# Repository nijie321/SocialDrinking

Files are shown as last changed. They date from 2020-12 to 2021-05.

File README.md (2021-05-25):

# PeerPub 
 Tracking two rats independently during oral operant self-administration of solutions (e.g. sucrose, alcohol, opioids).

## Program Structure

   Main Program: main.py (main_test.py) is the entry program. This program handles session command and rat ID
   scanning, adjusting the pump position, and finally calling the operant.py as a subprocess.
   Note that this program does not exit after calling the subprocess. It it kept alive, as the
   main thread, to record rat's ID when they poke their head near the antenna. Rat's ID are
   stored in _active and _inactive files located in the /home/pi/ directory.
   
   Operant Program: operant.py (operant_test.py) is the program which main invoke at the end of it's executation.
   This program handles saving each data point to corresponding data files.

   Pump Driver Program: pump_move.py is the program that is used, as a higher level abstraction, to drive the stepper motor using underlying gpiozero/RPi.GPIO library. This program mainly consist of the PumpMove class which contains a move() class for "rotating" the motor (forward and backward). The __del__ method need to be call at the end of each use to 'shutoff' the motor. This prevent the motor driver from overheating (there are more efficient ways to do this).
   
   Activity Counter Program: Rat's activity (inactive lick, active lick, and etc) are being represent as an instance of RatActivityCounter.

   PumpCalibration Program: Currently, the motor step size is not accurate enough. The pump's step need to be modified from time to time. This program prompt the user to measure the amount of solution the pump push out and enter that amount. Then the program will automatically re-adjust the step size.

## Configuration
   - Files

     - /home/pi/peerpub_config.json
        This file stores 3 information: device ID, session number/ID, and stepper motor step size. (The session number is increament by 1 each time the program start)

     - /home/pi/openbehavior/PeerPub/python/session_configuration.csv
        This file is used by the program to read in the session information. 

     - /home/pi/openbehavior/PeerPub/python/config.py
        This file stores different directory paths. Note that these path are all absolute paths. There's a "get_sessioninfo" function which takes in a argument "sessionid" to retrive session information from "session_configuration.csv" mentioned above. A good practice is to put related configuration functions in this file and import then when needed.

## Utility Scripts

   **check_empty_program.sh**: a script that check the size of every python file in the python/ directory. If one or more files are empty the script then reclone the entire repository.

   **check_network.sh**: a script that check the network connection right after the device boots up and ask user for action when the device was not able to connect to network.

## Program Overview
The main (main_test.py) program is used to read/scan the pre-configured command RFID stored in 'session_configuration.csv' file under python directory. After the command ID is scaned, the program proceed to ask for scanning rat's ID. The time between scanning rat's ID and command ID is the time for adjusting the pump position (e.g. after the rat's ID are scanned, the pump adjustment are disabled to avoid driver board overheating). After the rat's ID are scanned, the main program spawns a new operant (operant_test.py) program by passing in the necessary arguments and run it in the background. Note that because the operant program is a thread, the main program is kept alive (e.g. running in parallel with the operant program). The main program is tasked with reading the rat's ID when they poke their head into the active or inactve spout (disctinguished by the length of characters: 10 for inactive poke and 8 for active poke).

## Parts and GPIO Pin Connections Table

   [DRV8834 Low-Voltage Stepper Motor Driver](https://www.pololu.com/product/2134), [Stepper Motor](https://www.pololu.com/product/2267), [Belker Universal AC Adapter 3-12V](https://www.amazon.com/Belker-Adjustable-Universal-Household-Electronics/dp/B07NKZCWT1/ref=asc_df_B07NKZCWT1/?tag=hyprod-20&linkCode=df0&hvadid=366402536789&hvpos=&hvnetw=g&hvrand=9548953669677245441&hvpone=&hvptwo=&hvqmt=&hvdev=c&hvdvcmdl=&hvlocint=&hvlocphy=9013532&hvtargid=pla-800552094134&psc=1&tag=&ref=&adgrpid=75347436439&hvpone=&hvptwo=&hvadid=366402536789&hvpos=&hvnetw=g&hvrand=9548953669677245441&hvqmt=&hvdev=c&hvdvcmdl=&hvlocint=&hvlocphy=9013532&hvtargid=pla-800552094134)
   | Pins on the driver | GPIO pin slot on the Pi, external power supply, and the stepper motor|
   |--------------------|------------------------|
   |      VMOT         |      **AC Adapter** - positive end of LED Terminal Adapter    |
   |     GND |   **AC Adapter** - negative end of LED Terminal Adapter |
   | B2, B1, A1, A2 |    **Stepper Motor** - Black, Green, Red, and Blue wire respectively      |
   |      GND |    **Pi** - Any GND pin                |
   |      M0, M1 | **Pi** - GPIO 17 and 22       |
   |     SLP | **Pi** - Any 3v3 pin          |
   |      STEP | **Pi** - GPIO 6            |
   |      DIR | **Pi** - GPIO 26 |
   
   [Adafruit 12-Key Capacitive Touch Sensor - MPR121](https://www.adafruit.com/product/1982)
   | Pins on the driver | GPIO pin slot on the Pi and external wires|
   |--------------------|------------------------|
   |  SCL, SDA | **Pi** - GPIO 3 and 2 respectively |
   |  3Vo | **Pi** - Any 3v3 pin|
   |  GND | **Pi** - Any GND pin|
   |  0 | **external wire** - inactive wire|
   |  1 | **external wire** - active wire|

   [Limit Switch](https://www.amazon.com/MXRS-Hinge-Momentary-Button-Switch/dp/B07MW2RPJY/ref=lp_5739467011_1_7)
   | Pins on the driver | GPIO pin slot on the Pi and external wires|
   |--------------------|------------------------|
   |  Normally Open (NO) | **Pi** - any GND pin|
   |  Forward Limit - Contact Point (C) | **Pi** - GPIO 24|
   |  Backward Limit - Contact Point (C) | **Pi** - GPIO 23|

   [Push Button](https://www.amazon.com/DAOKI-Miniature-Momentary-Tactile-Quality/dp/B01CGMP9GY/ref=asc_df_B01CGMP9GY/?tag=hyprod-20&linkCode=df0&hvadid=309774137275&hvpos=&hvnetw=g&hvrand=7843520885449353644&hvpone=&hvptwo=&hvqmt=&hvdev=c&hvdvcmdl=&hvlocint=&hvlocphy=9013532&hvtargid=pla-640514760452&psc=1)
   | Pins on the driver | GPIO pin slot on the Pi|
   |--------------------|------------------------|
   | Forward Button | **Pi** - GPIO 5|
   | Backward Button | **Pi** - GPIO 27|
   **Connect resistor and GND correspondingly**
   
   [Pixel Ring](https://www.adafruit.com/product/1643)
   | Pins on the driver | GPIO pin slot on the Pi|
   |--------------------|------------------------|
   | IN | **Pi** - GPIO 18|
   | GND | **Pi** - any GND pin |
   | 5V DC | **Pi** - any 5V pin |

## Resources
   [Raspberry Pi Stepper Motor Tutorial](https://www.rototron.info/raspberry-pi-stepper-motor-tutorial/)  
   [Raspberry Pi Stepper Motor Control with nema17](https://makersportal.com/blog/raspberry-pi-stepper-motor-control-with-nema-17)  
   [OpenSourceSyringePump](http://cavarnon.com/syringepump)  
   [How to Control a stepper motor with DRV8825 driver and Arduino](https://www.makerguides.com/drv8825-stepper-motor-driver-arduino-tutorial/)

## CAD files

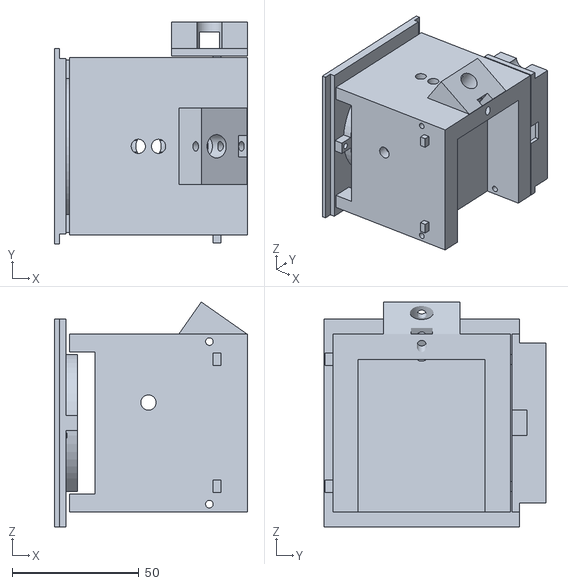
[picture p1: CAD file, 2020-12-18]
openscad/rfid_waterspout_complete.stl
76.0 x 87.5 x 88.6

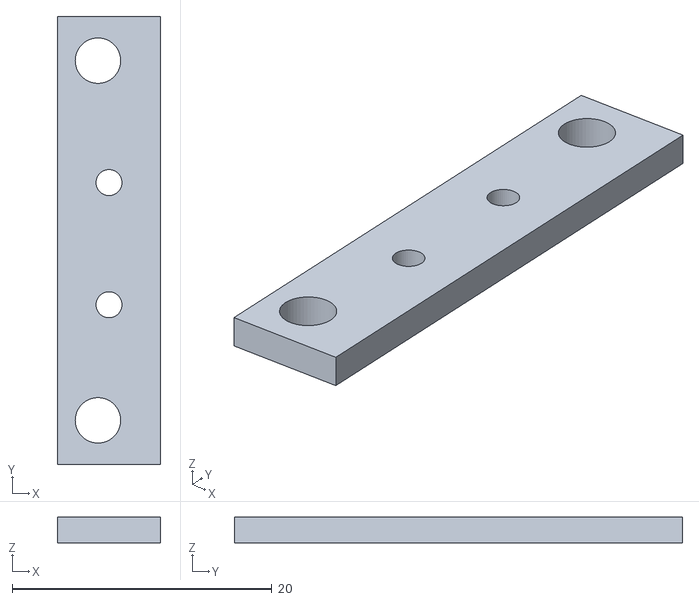
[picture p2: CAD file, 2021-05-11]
openscad/limit_button_mount.stl
7.90 x 34.5 x 2.00

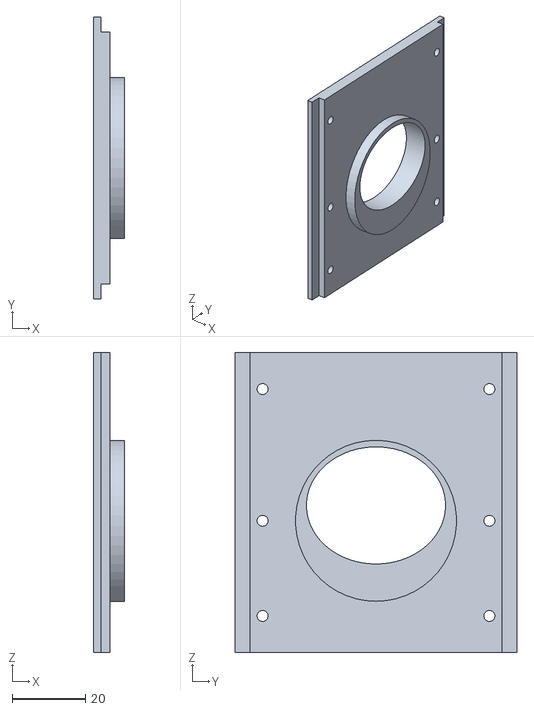
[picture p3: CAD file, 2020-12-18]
openscad/rfid_waterspout_front_panel.stl
8.50 x 77.0 x 82.0

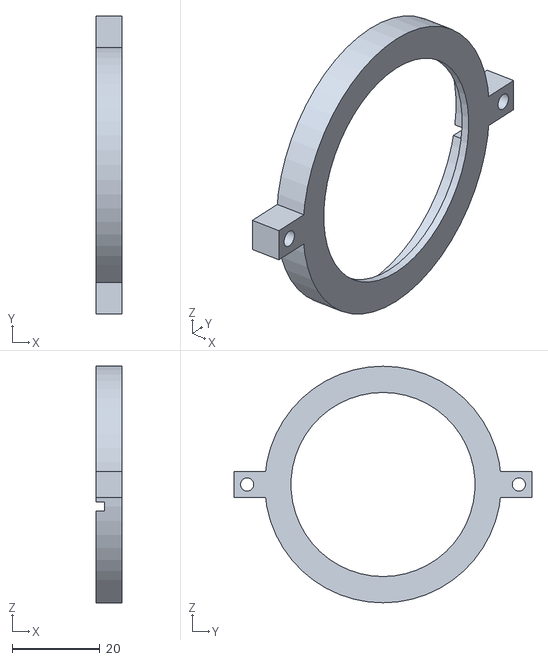
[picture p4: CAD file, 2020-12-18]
openscad/rfid_waterspout_ring_cover.stl
6.00 x 68.0 x 54.0

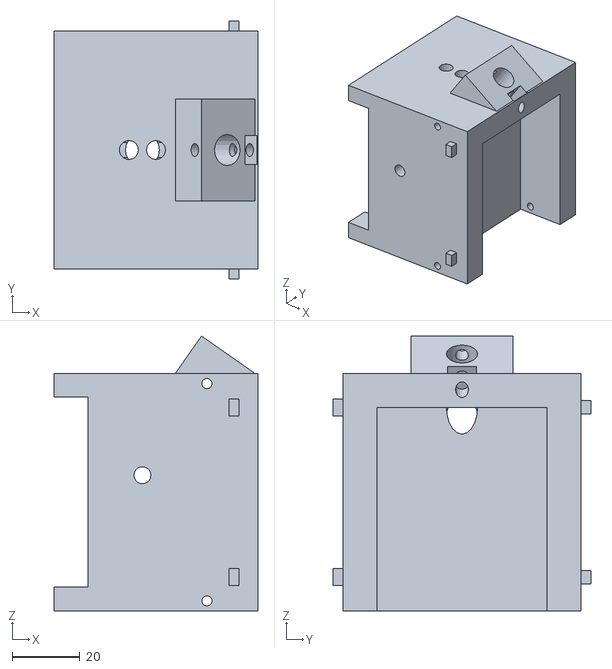
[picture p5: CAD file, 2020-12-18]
openscad/rfid_waterspout_holder.stl
60.0 x 76.0 x 81.0

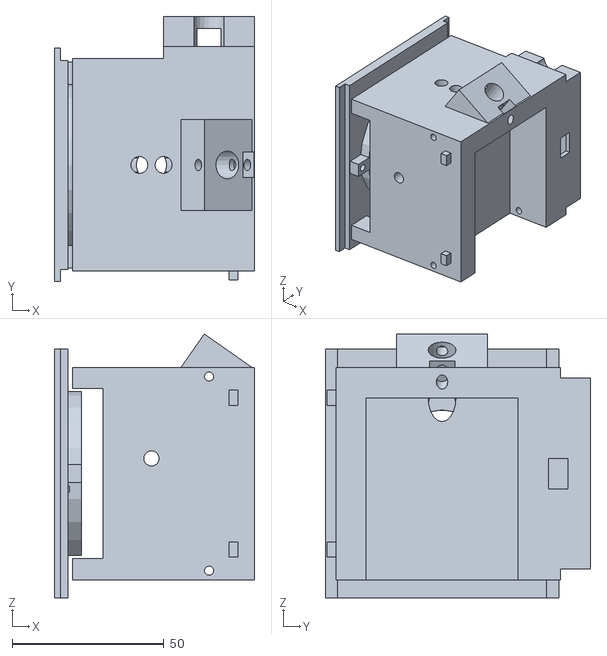
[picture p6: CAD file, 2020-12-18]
openscad/rfid_waterspout_entire_unit.stl
66.0 x 87.5 x 87.0

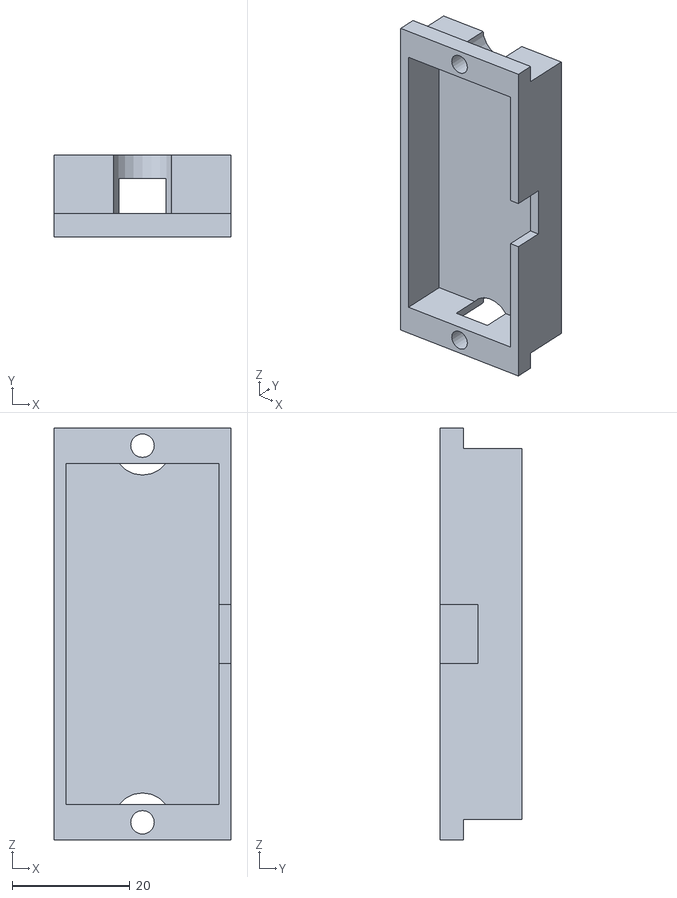
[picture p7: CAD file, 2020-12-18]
openscad/rfid_water_spout_cboard_cover.stl
30.0 x 14.0 x 70.0

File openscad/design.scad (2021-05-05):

$fn=50;


height=59.35 - 2.4;
width=47.60;
thickness=10.65;

topWidth=38.29;
topHeight=23.70;
bottomWidth=31.10;
bottomHeight=height-topHeight;
thickness3=6.57;



diameter=28.88;



circleThickness=2;
radius=diameter/2 + 1;

smallRecHeight=8.38;
smallRecWidth=3.33;
cuttingWidth=23.59;
cuttingHeight=14.69;
extraHeight = (height - (smallRecHeight + cuttingHeight));
extraWidth = 3.63;

bigCircleDiameter=27.33;
topHalfHeight=29.63;
remaindingHeight=height-topHalfHeight;

hex_nut_diameter=7.89 + 1.6; // +1.6, 
hex_nut_radius=hex_nut_diameter/2;
hex_nut_thickness=3.85;

hex_nut_inner_diameter= 5.8;//5;
hex_nut_inner_radius=hex_nut_inner_diameter/2 + .4;



temp=(thickness/2) - (thickness - thickness3);
offsetFromCenter=19; //19.25; //1.5 // 2.3
hexNutGroveExtraDepth=2;

screwRadius=1.75;
screwDepth=9.35;

module part1(){
translate([(width/2) - (topWidth/2) ,(thickness/2) - (thickness3)/2,0]) color("blue") difference(){    
    difference(){
cube([topWidth, thickness3, height], center=true);  

union(){
color("blue") translate([topWidth/2 - (extraWidth/2),0,-extraHeight/2 + ( (height/2) - (smallRecHeight + cuttingHeight) )]) cube([extraWidth,thickness3 ,extraHeight],center=true);

color("blue") translate([ -(topWidth/2 - (extraWidth/2)),0,-extraHeight/2 + ( (height/2) - (smallRecHeight + cuttingHeight) )]) cube([extraWidth,thickness3 ,extraHeight],center=true);
}


//translate([0,0,extraHeight - (height/2) - offsetFromCenter]) union(){
//    //-(remaindingHeight/2) + (hex_nut_radius)
//translate([0,5,0]) color("black") rotate([90,0,0]) cylinder(h=hex_nut_thickness/2 + hexNutGroveExtraDepth + 1.3, r=hex_nut_radius,center=true, $fn = 6); //h=thickness3
////-(remaindingHeight/2) + (hex_nut_inner_radius + (hex_nut_radius - hex_nut_inner_radius))
//translate([0, 0,0]) color("red") rotate([90,0,0]) cylinder(h=hex_nut_thickness/2 + 10, r=hex_nut_inner_radius,center=true, $fn = 6);
//}


}
union(){
    translate([0,-((-(thickness3/2)+(thickness3-circleThickness)/2)),(height/2) - (smallRecHeight + cuttingHeight) ]) union(){
translate([0,0,(cuttingHeight/2) + (smallRecHeight)]) cube([cuttingWidth,thickness3 - circleThickness +.1, cuttingHeight],center=true);
                 translate([0,0,smallRecHeight/2]) cube([smallRecWidth,thickness3 - circleThickness+.1,smallRecHeight],center=true);            
}


translate([0,-(thickness3/2 - (circleThickness/2)),(height/2) - (radius)]) color("red")rotate([90,0,0])union(){
        cylinder(h=circleThickness, r=radius, center=true);
        translate([0,radius/2,0])cube([radius*2,radius,circleThickness],center=true);
    }
    
    }

}
}


module part2(){
//translate([0,temp,0]) 
difference(){
cube([width,thickness,height],center=true);
//translate([0,(thickness/2) - (thickness - thickness3)/2,0]) color("blue") cube([topWidth,thickness - thickness3,height],center=true);
//
translate([(width/2) - (topWidth/2),(thickness/2) - (thickness3)/2,0]) color("blue") union(){
cube([topWidth, thickness3, height], center=true);   
union(){
color("red") translate([topWidth/2 - (extraWidth/2),0,-extraHeight/2 + ( (height/2) - (smallRecHeight + cuttingHeight) )]) cube([extraWidth,thickness3+10 ,extraHeight],center=true);

color("red") translate([ -(topWidth/2 - (extraWidth/2)),0,-extraHeight/2 + ( (height/2) - (smallRecHeight + cuttingHeight) )]) cube([extraWidth,thickness3+10,extraHeight],center=true);
}


//translate([0,0, extraHeight - (height/2)  - offsetFromCenter]) union(){
//    
//translate([0, -temp - (hex_nut_thickness/2) - .8,0]) color("red") rotate([90,0,0]) cylinder(h=hex_nut_thickness/2 + hexNutGroveExtraDepth, r=hex_nut_radius,center=true, $fn = 6);
//
//translate([0, -temp - (hex_nut_thickness/2),0]) color("red") rotate([90,0,0]) cylinder(h=hex_nut_thickness/2 + 7, r=hex_nut_inner_radius,center=true, $fn = 6);
//}


}
}

}

module glueScrews(){
translate([0,0.1,0]) union(){
rotate([90,0,0]) translate([(width/2) - (topWidth/2) - (topWidth/4),-(height/3),-(thickness-screwDepth)/2]) cylinder(h=screwDepth,r=screwRadius,center=true);

rotate([90,0,0]) translate([(width/2) - (topWidth/2) + (topWidth/4),-(height/9),-(thickness-screwDepth)/2]) cylinder(h=screwDepth,r=screwRadius,center=true);
}
}


module modifiedParts(part=1){


difference(){
    
        if(part == 1){
            part1();
        }else if(part == 2){
            part2();
        }
//        part2();    

    
//translate([(width/2) - (topWidth/2),0,extraHeight - (height/2) - offsetFromCenter]) union(){
//    //-(remaindingHeight/2) + (hex_nut_radius)
//    
//    //((hex_nut_thickness/2 + 10)/2)-(hex_nut_thickness/2 + hexNutGroveExtraDepth + 1.3)/2
//
//    
////-(remaindingHeight/2) + (hex_nut_inner_radius + (hex_nut_radius - hex_nut_inner_radius))
//
//
//translate([0,0,0]) color("black") rotate([90,0,0]) cylinder(h=hex_nut_thickness, r=hex_nut_radius,center=true, $fn = 6); //h=thickness3
//
//translate([0, 0,0]) color("red") rotate([90,0,0]) cylinder(h=hex_nut_thickness+ 20, r=hex_nut_inner_radius,center=true, $fn = 6);
//    
//
////    glueScrews();
//}

}
}

//translate([3.5,11,0]) cylinder(d=21.95,h=3.5,$fn=50,center=true);

//translate([(width/2) - (topWidth/2),-(extraHeight - (height/2) - offsetFromCenter),0]) cylinder(d=21.95,h=3.5,$fn=50,center=true);

//union(){
//translate([(width/2) - (topWidth/2),-(extraHeight - (height/2) - offsetFromCenter)-7.75,0]) cylinder(h=15,d=3.75,center=true);
//translate([(width/2) - (topWidth/2) -7.75,-(extraHeight - (height/2) - offsetFromCenter),0]) cylinder(h=15,d=3.75,center=true);
//translate([(width/2) - (topWidth/2) +7.75,-(extraHeight - (height/2) - offsetFromCenter),0]) cylinder(h=15,d=3.75,center=true);
//translate([(width/2) - (topWidth/2) ,-(extraHeight - (height/2) - offsetFromCenter) + 7.75,0]) cylinder(h=15,d=3.75,center=true);
//}


//rotate([-90,0,0]) difference(){
//modifiedParts(1);
//   glueScrews(); 
//}

//rotate([90,0,0]) translate([(width/2) - (topWidth/2),-(0),extraHeight - (height/2) - offsetFromCenter]) cylinder(d=21.95,h=3.5,$fn=50,center=true);

//rotate([90,0,0]) modifiedParts(1);

difference(){
difference(){
rotate([90,0,0]) difference(){

modifiedParts(2);
//    translate([(width/2) - (topWidth/2),-(extraHeight - (height/2) - offsetFromCenter),0]) cylinder(d=21.95,h=3.5,$fn=50,center=true);
//    glueScrews();
    
}

difference(){
//translate([0,0,.85])
    union(){
//translate([(width/2) - (topWidth/2),-(extraHeight - (height/2) - offsetFromCenter) ,-1.5]) cylinder(d=21.95 + .2,h=3.5,$fn=50,center=true);
//    
//    translate([(width/2) - (topWidth/2),-(extraHeight - (height/2) - offsetFromCenter),0]) cylinder(h=15,d=10 + .2,center=true);
    
    translate([(width/2) - (topWidth/2),-(extraHeight - (height/2) - offsetFromCenter) ,-1.5]) cylinder(d=21.95 + .2,h=3.5,$fn=50,center=true);
    
    translate([(width/2) - (topWidth/2),-(extraHeight - (height/2) - offsetFromCenter),0]) cylinder(h=15,d=10 + .2,center=true);
}


}

}


union(){
translate([(width/2) - (topWidth/2),-(extraHeight - (height/2) - offsetFromCenter)-7.75 ,0]) cylinder(h=15,d=3.75 - .4,center=true);
translate([(width/2) - (topWidth/2) -7.75 ,-(extraHeight - (height/2) - offsetFromCenter),0]) cylinder(h=15,d=3.75 - .4,center=true);
translate([(width/2) - (topWidth/2) ,-(extraHeight - (height/2) - offsetFromCenter) + 7.75 ,0]) cylinder(h=15,d=3.75 - .4,center=true);
translate([(width/2) - (topWidth/2) +7.75 ,-(extraHeight - (height/2) - offsetFromCenter),0]) cylinder(h=15,d=3.75 - .4,center=true);

}

}

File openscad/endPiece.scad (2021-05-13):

pumpHolderWidth=50.25;
pumpHolderHeight=38.17;
pumpHolderThickness=10.15;


semiCircleDiameter=22; //16.36;
semiCircleRadius=semiCircleDiameter/2;

semiCircleHeight=26.54;
semiCircleThickness=7.23;


//difference(){
//    cube([pumpHolderWidth,pumpHolderThickness,pumpHolderHeight],center=true);
//
//    translate([0,(pumpHolderThickness/2)-(semiCircleThickness/2)+.001,(pumpHolderHeight/2) - (semiCircleHeight/2)]) color("red") union(){
//    rotate([90,0,0]) cylinder(h=pumpHolderThickness+5,r=semiCircleRadius, center=true);
//
//    color("red") translate([0,0,(semiCircleHeight/2)/2]) cube([semiCircleDiameter,pumpHolderThickness+5,semiCircleHeight/2],center=true);
//    }
//}

recHeight=32.96;
recWidth=33.45;
recThickness=6.3;

sideScrewDiameter=3.5;
sideScrewRadius=sideScrewDiameter/2;
sideScrewDepth=4.65;



cubeShape=6.38;


topPlateHeight= 23.44;//1.45;
topPlateOffset = 1.45;

module sideScrew(){
    cylinder(h=sideScrewDepth,r=sideScrewRadius,center=true);
}

module makeFourSideScrews(){
union(){
color("red") translate([(recWidth/2)-(sideScrewDepth/2),0,(recHeight/2) - (cubeShape/2)]) rotate([0,090,0]) sideScrew();
color("red") translate([-((recWidth/2)-(sideScrewDepth/2)),0,(recHeight/2) - (cubeShape/2)]) rotate([0,090,0]) sideScrew();

color("red") translate([((recWidth/2)-(sideScrewDepth/2)),0,-((recHeight/2) - (cubeShape/2))]) rotate([0,090,0]) sideScrew();
color("red") translate([-((recWidth/2)-(sideScrewDepth/2)),0,-((recHeight/2) - (cubeShape/2))]) rotate([0,090,0]) sideScrew();   
}

}




module endPieceBlock(){
difference(){
cube([recWidth,recThickness,recHeight],center=true);
makeFourSideScrews();
}
}


hookWidth=12;//7.40;
hookHeight=7;
hookThickness=5;

stopperWidth=(1/2)*hookWidth;
stopperHeight=(1/2)*hookHeight;


module recStopper(){
//difference(){
//    //hookHeight+2
//cube([hookWidth,recThickness,hookHeight+2],center=true);
//
//translate([(stopperWidth/2) + (hookWidth/2)-(stopperWidth),0,-stopperHeight/2]) union(){
//cube([stopperWidth,recThickness,stopperHeight],center=true);
//color("blue") translate([-((1/2)*stopperWidth)/2,0,2*((stopperHeight-1)/2)]) cube([(1/2)*stopperWidth,hookThickness,stopperHeight-1],center=true);
//}
//}

difference(){
cube([hookWidth,recThickness,hookHeight+2],center=true);
    translate([1.5,0,-(hookHeight/1.5)/2]) cube([hookWidth/4,recThickness,hookHeight/1.2],center=true);
}
}




module circleStopper(){
difference(){
rotate([90,0,0]) cylinder(h=recThickness,r=5,center=true,$fn=50);
union(){
rotate([90,0,0]) cylinder(h=recThickness,r=2.5,center=true,$fn=50);
translate([-(2.5/2)-(2.5),0,0]) cube([2.5+.1,recThickness,0.8],center=true);
}
}
}

module pumpHolder(){
translate([0,0,(topPlateHeight/2) + recHeight/2 ]) union(){
difference(){
    color("red") cube([recWidth,recThickness,topPlateHeight ],center=true);

translate([0,0,-(topPlateHeight/2)+(semiCircleRadius) +topPlateOffset+5 + 2.75]) union(){
translate([0,0, semiCircleRadius/2]) cube([semiCircleDiameter,recThickness,semiCircleRadius],center=true); //topPlateHeight/2+5
rotate([90,0,0]) cylinder(h=recThickness,r=semiCircleRadius,center=true);
}

}
union(){
translate([(hookWidth/2)+(recWidth/2),0,((hookHeight+2)/2)]) recStopper();

translate([-5 - (recWidth/2) +1,0,((hookHeight+2)/2)]) circleStopper();
}
}
}



module endPiece(){
    union(){
        endPieceBlock();
        pumpHolder();
    }
}



difference(){

    endPiece();
       height=59.35 - 2.4;
width=47.60;
thickness=10.65;

topWidth=38.29;
topHeight=23.70;
bottomWidth=31.10;
bottomHeight=height-topHeight;
thickness3=6.57;



diameter=28.88;



circleThickness=2;
radius=diameter/2 + 1;

smallRecHeight=8.38;
smallRecWidth=3.33;
cuttingWidth=23.59;
cuttingHeight=14.69;
extraHeight = (height - (smallRecHeight + cuttingHeight));
extraWidth = 3.63;

bigCircleDiameter=27.33;
topHalfHeight=29.63;
remaindingHeight=height-topHalfHeight;

hex_nut_diameter=7.89 + 1.6; // +1.6, 
hex_nut_radius=hex_nut_diameter/2;
hex_nut_thickness=3.85;

hex_nut_inner_diameter= 5.8;//5;
hex_nut_inner_radius=hex_nut_inner_diameter/2 + .4;



temp=(thickness/2) - (thickness - thickness3);
offsetFromCenter=19; //19.25; //1.5 // 2.3
hexNutGroveExtraDepth=2;

screwRadius=1.75;
screwDepth=9.35;

translate([-4.5,0,-17+1.9 + 1 ]) union(){
    rotate([90,0,0]) translate([(width/2) - (topWidth/2),-(extraHeight - (height/2) - offsetFromCenter) ,-1.5]) cylinder(d=21.95 + .1,h=7,$fn=50,center=true);
    
    rotate([90,0,0]) translate([(width/2) - (topWidth/2),-(extraHeight - (height/2) - offsetFromCenter),0]) cylinder(h=15,d=10 + .2 ,$fn=50,center=true);
    
//    rotate([90,0,0]) union(){
//translate([(width/2) - (topWidth/2),-(extraHeight - (height/2) - offsetFromCenter)-7.75 ,0]) cylinder(h=15,d=3.75,$fn=50,center=true);
//translate([(width/2) - (topWidth/2) -7.75 ,-(extraHeight - (height/2) - offsetFromCenter),0]) cylinder(h=15,d=3.75,$fn=50,center=true);
//translate([(width/2) - (topWidth/2) +7.75 ,-(extraHeight - (height/2) - offsetFromCenter),0]) cylinder(h=15,d=3.75,$fn=50,center=true);
//translate([(width/2) - (topWidth/2) ,-(extraHeight - (height/2) - offsetFromCenter) + 7.75 ,0]) cylinder(h=15,d=3.75,$fn=50,center=true);
//}
    
}

}


//difference(){
//    height=59.35 - 2.4;
//width=47.60;
//thickness=10.65;
//
//topWidth=38.29;
//topHeight=23.70;
//bottomWidth=31.10;
//bottomHeight=height-topHeight;
//thickness3=6.57;
//
//
//
//diameter=28.88;
//
//
//
//circleThickness=2;
//radius=diameter/2 + 1;
//
//smallRecHeight=8.38;
//smallRecWidth=3.33;
//cuttingWidth=23.59;
//cuttingHeight=14.69;
//extraHeight = (height - (smallRecHeight + cuttingHeight));
//extraWidth = 3.63;
//
//bigCircleDiameter=27.33;
//topHalfHeight=29.63;
//remaindingHeight=height-topHalfHeight;
//
//hex_nut_diameter=7.89 + 1.6; // +1.6, 
//hex_nut_radius=hex_nut_diameter/2;
//hex_nut_thickness=3.85;
//
//hex_nut_inner_diameter= 5.8;//5;
//hex_nut_inner_radius=hex_nut_inner_diameter/2 + .4;
//
//
//
//temp=(thickness/2) - (thickness - thickness3);
//offsetFromCenter=19; //19.25; //1.5 // 2.3
//hexNutGroveExtraDepth=2;
//
//screwRadius=1.75;
//screwDepth=9.35;
//difference(){
////union(){
//translate([(width/2) - (topWidth/2),-(extraHeight - (height/2) - offsetFromCenter) ,-1.5]) cylinder(d=21.95 + .2,h=3.5,$fn=50,center=true);
//    
//    translate([(width/2) - (topWidth/2),-(extraHeight - (height/2) - offsetFromCenter),0]) cylinder(h=15,d=10 + .2 ,$fn=50,center=true);
////}
//
//
//}
//
//
//
//
//union(){
//translate([(width/2) - (topWidth/2),-(extraHeight - (height/2) - offsetFromCenter)-7.75 ,0]) cylinder(h=15,d=3.75,$fn=50,center=true);
//translate([(width/2) - (topWidth/2) -7.75 ,-(extraHeight - (height/2) - offsetFromCenter),0]) cylinder(h=15,d=3.75,$fn=50,center=true);
//translate([(width/2) - (topWidth/2) +7.75 ,-(extraHeight - (height/2) - offsetFromCenter),0]) cylinder(h=15,d=3.75,$fn=50,center=true);
//translate([(width/2) - (topWidth/2) ,-(extraHeight - (height/2) - offsetFromCenter) + 7.75 ,0]) cylinder(h=15,d=3.75,$fn=50,center=true);
//}
//
//}







//difference(){
//    //hookHeight+2
//%cube([hookWidth,recThickness,hookHeight+2],center=true);
//
//translate([(stopperWidth/2) + (hookWidth/2)-(stopperWidth),0,-stopperHeight/2]) union(){
//%cube([stopperWidth,recThickness,stopperHeight],center=true);
////color("blue") translate([-((1/2)*stopperWidth)/2,0,2*((stopperHeight-1)/2)]) 
//    color("blue") cube([(1/2)*stopperWidth,hookThickness,stopperHeight-1],center=true);
//}
//}



//translate([stopperWidth/2,0,-((hookHeight+2)/4)]) %cube([stopperWidth,recThickness,(hookHeight+2)/2],center=true);
////color("blue") translate([-((1/2)*stopperWidth)/2,0,2*((stopperHeight-1)/2)]) 
//    color("blue") cube([(1/2)*stopperWidth,hookThickness,stopperHeight-1],center=true);

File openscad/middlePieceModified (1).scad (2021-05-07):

pumpHolderWidth=50.25;
pumpHolderHeight=36;//38.26;
pumpHolderThickness=10.20;


semiCircleDiameter=19; //16.36;
semiCircleRadius=semiCircleDiameter/2;

semiCircleHeight=26.54;
semiCircleThickness=7.23;

recBlockHeight=13.63;
recBlockWidth=8.25 + 3;

offsetThickness=2.03;



sideScrewRadius=1.75;
sideScrewHeight=4;
sideScrewOffsetRatio=0.38;

// 6.3
//offset1=2;
//translate([0,-20,0]) rotate([-90,0,0]) union(){
//color("red") rotate([90,0,0]) cylinder(h=recBlockWidth,r=11+offset1,center=true);
//translate([0,0,(11+offset1)/2]) cube([22+offset1*2, recBlockWidth, 11+offset1],center=true);
//}

rotate([90,0,0]) scale([0.94,1,1]) translate([0,0,0]) difference(){
minkowski(){
    
difference(){
difference(){
difference(){
    cube([pumpHolderWidth,pumpHolderThickness,pumpHolderHeight],center=true);

    offset1=1.7;
    translate([0,0,7 + 4.85 ]) rotate([0,0,0]) union(){
        rotate([90,0,0]) cylinder(h=recBlockWidth,r=11+offset1 ,center=true);
        translate([0,0,(11 + offset1 )/2]) cube([22 + offset1*2, recBlockWidth, 11 + offset1 ],center=true);
    }
    
//    translate([0,(pumpHolderThickness/2)-(semiCircleThickness/2)+.001,(pumpHolderHeight/2) - (semiCircleHeight/2) + .5]) color("red") union(){
//        
//        
//    rotate([90,0,0]) cylinder(h=pumpHolderThickness+5,r=semiCircleRadius, center=true);
//
//    color("blue") translate([0,0,(semiCircleHeight/2)/2]) cube([semiCircleDiameter,pumpHolderThickness+5,semiCircleHeight/2 +.1],center=true);
//        
//        
//        
//    }
}

union(){
color("red") translate([(pumpHolderWidth/2)-(recBlockWidth/2),0,-(pumpHolderHeight/2)+(recBlockHeight/2)]) cube([recBlockWidth,pumpHolderThickness,recBlockHeight],center=true);

color("red") translate([-((pumpHolderWidth/2)-(recBlockWidth/2)),0,-(pumpHolderHeight/2)+(recBlockHeight/2)]) cube([recBlockWidth,pumpHolderThickness,recBlockHeight],center=true);
}

}

translate([0,(pumpHolderThickness/2)-(offsetThickness/2),(pumpHolderHeight-recBlockHeight)/2 - ((pumpHolderHeight/2) - recBlockHeight)]) color("black") cube([pumpHolderWidth-3,offsetThickness,pumpHolderHeight-recBlockHeight],center=true);

}


cylinder(1,center=true,$fn=50);
    
}
    union(){
        screwZAxisoffSet=2.15;
        color("red") translate([pumpHolderWidth/2 - (recBlockWidth/2) - (sideScrewHeight/2)-3.1,0,(pumpHolderHeight/2) + 1/2 -(pumpHolderHeight-recBlockHeight) - (sideScrewOffsetRatio*recBlockHeight) - screwZAxisoffSet]) rotate([0,90,0]) cylinder(h=sideScrewHeight,r=sideScrewRadius,$fn=50,center=true);

color("red") translate([-(pumpHolderWidth/2 - (recBlockWidth/2) - (sideScrewHeight/2)-3.1  ),0,(pumpHolderHeight/2) + 1/2 -(pumpHolderHeight-recBlockHeight) - (sideScrewOffsetRatio*recBlockHeight) - screwZAxisoffSet]) rotate([0,90,0]) cylinder(h=sideScrewHeight,r=sideScrewRadius,$fn=50,center=true);
    }
}



//color("red") translate([20,10,-9]) 
//difference(){

screwZAxisoffSet=2.15;

difference(){
difference(){
    color("red") translate([pumpHolderWidth/2 - (recBlockWidth) +1,pumpHolderHeight/2 - (7),-9]) cube([2.8,8,28.5],center=true);
    
rotate([90,0,0]) scale([0.94,1,1]) color("blue") translate([pumpHolderWidth/2 - (recBlockWidth/2) - (sideScrewHeight/2)-3.1 + sideScrewHeight -1.6 ,0,(pumpHolderHeight/2) + 1/2 -(pumpHolderHeight-recBlockHeight) - (sideScrewOffsetRatio*recBlockHeight) - screwZAxisoffSet]) rotate([0,90,0]) cylinder(h=sideScrewHeight,r=sideScrewRadius,$fn=50,center=true);

}
rotate([90,0,0]) scale([0.94,1,1]) color("blue") translate([pumpHolderWidth/2 - (recBlockWidth/2) - (sideScrewHeight/2)-3.1 + sideScrewHeight -1.6 ,0 -19,(pumpHolderHeight/2) + 1/2 -(pumpHolderHeight-recBlockHeight) - (sideScrewOffsetRatio*recBlockHeight) - screwZAxisoffSet]) rotate([0,90,0]) cylinder(h=sideScrewHeight + 1,r=sideScrewRadius,$fn=50,center=true);
}


difference(){
difference(){
    color("red") translate([-(pumpHolderWidth/2 - (recBlockWidth) +1),pumpHolderHeight/2 - (7),-9]) cube([2.8,8,28.5],center=true);
    
rotate([90,0,0]) scale([0.94,1,1]) color("blue") translate([-(pumpHolderWidth/2 - (recBlockWidth/2) - (sideScrewHeight/2)-3.1 + sideScrewHeight -1.6) ,0 ,(pumpHolderHeight/2) + 1/2 -(pumpHolderHeight-recBlockHeight) - (sideScrewOffsetRatio*recBlockHeight) - screwZAxisoffSet]) rotate([0,90,0]) cylinder(h=sideScrewHeight,r=sideScrewRadius,$fn=50,center=true);

}

rotate([90,0,0]) scale([0.94,1,1]) color("blue") translate([-(pumpHolderWidth/2 - (recBlockWidth/2) - (sideScrewHeight/2)-3.1 + sideScrewHeight -1.6) ,0 - 19 ,(pumpHolderHeight/2) + 1/2 -(pumpHolderHeight-recBlockHeight) - (sideScrewOffsetRatio*recBlockHeight) - screwZAxisoffSet]) rotate([0,90,0]) cylinder(h=sideScrewHeight + 1,r=sideScrewRadius,$fn=50,center=true);
}







//rotate([90,0,0]) scale([0.94,1,1])    union(){
//        screwZAxisoffSet=2.15;
//        color("blue") translate([pumpHolderWidth/2 - (recBlockWidth/2) - (sideScrewHeight/2)-3.1 + sideScrewHeight ,0,(pumpHolderHeight/2) + 1/2 -(pumpHolderHeight-recBlockHeight) - (sideScrewOffsetRatio*recBlockHeight) - screwZAxisoffSet]) rotate([0,90,0]) cylinder(h=sideScrewHeight,r=sideScrewRadius,$fn=50,center=true);
//
//color("blue") translate([-(pumpHolderWidth/2 - (recBlockWidth/2) - (sideScrewHeight/2)-3.1  ) - sideScrewHeight,0,(pumpHolderHeight/2) + 1/2 -(pumpHolderHeight-recBlockHeight) - (sideScrewOffsetRatio*recBlockHeight) - screwZAxisoffSet]) rotate([0,90,0]) cylinder(h=sideScrewHeight,r=sideScrewRadius,$fn=50,center=true);
//    }
//    
//    union(){
//    color("red") translate([pumpHolderWidth/2 - (recBlockWidth) +1,pumpHolderHeight/2 - (7),-9]) cube([2.5,8,28.5],center=true);
//
//    color("red") translate([-(pumpHolderWidth/2 - (recBlockWidth) +1),pumpHolderHeight/2 - (7),-9]) cube([2.5,8,28.5],center=true);
//    }
//}


////pumpHolderWidth
////recBlockWidth/2 + (sideScrewHeight/2)
//color("red") translate([pumpHolderWidth/2 - (recBlockWidth/2) - (sideScrewHeight/2)-3.1,0,(pumpHolderHeight/2) + 1/2 -(pumpHolderHeight-recBlockHeight) - (sideScrewOffsetRatio*recBlockHeight)]) rotate([0,90,0]) cylinder(h=sideScrewHeight,r=sideScrewRadius,$fn=50,center=true);
//
//color("red") translate([-(pumpHolderWidth/2 - (recBlockWidth/2) - (sideScrewHeight/2)-3.1 ),0,(pumpHolderHeight/2) + 1/2 -(pumpHolderHeight-recBlockHeight) - (sideScrewOffsetRatio*recBlockHeight)]) rotate([0,90,0]) cylinder(h=sideScrewHeight,r=sideScrewRadius,$fn=50,center=true);
////cube([60,1,1],center=true);
//
//
//color("blue") translate([0,0,recBlockHeight/2]) cube([recBlockWidth, pumpHolderThickness,recBlockHeight],center=true);
//minkowski(){
//    translate([0,0,recBlockHeight/2]) cube([recBlockWidth, pumpHolderThickness,recBlockHeight],center=true);
//    cylinder(.00000000001,center=true,$fn=50);
//}



//-----------------------------------------

//translate([0,(pumpHolderThickness/2)-(offsetThickness/2),(pumpHolderHeight-recBlockHeight)/2 - ((pumpHolderHeight/2) - recBlockHeight)]) color("black") cube([pumpHolderWidth-3,offsetThickness,pumpHolderHeight-recBlockHeight],center=true);

//
//difference(){
//    %cube([pumpHolderWidth,pumpHolderThickness,pumpHolderHeight],center=true);
//
//    translate([0,(pumpHolderThickness/2)-(semiCircleThickness/2)+.001,(pumpHolderHeight/2) - (semiCircleHeight/2)]) color("red") union(){
//    rotate([90,0,0]) cylinder(h=pumpHolderThickness+5,r=semiCircleRadius, center=true);
//
//    color("red") translate([0,0,(semiCircleHeight/2)/2]) cube([semiCircleDiameter,pumpHolderThickness+5,semiCircleHeight/2 +.1],center=true);
//    }
//}

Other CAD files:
openscad/rfid_waterspout.scad

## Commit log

2021-03-18 modify pump test. 5 touches reward activation
2021-03-18 motor step config
2021-03-18 fix pump test
2021-04-05 use csv configuration file
    [session_configuration.csv]
2021-04-20 add pump calibration
2021-04-23 pump calibration change
2021-04-23 rename pump test to pump calibration
2021-04-27 reduce the frequency help smooth the motor rotation
2021-04-28 change pump config file format
2021-04-29 add syringe empty to the summary file
2021-04-29 lower the pump when syringe emptied
2021-05-11 add limit button 3d printing
    [limit_button_mount.stl]
2021-05-19 add GPIO pin connection instructions
2021-07-15 add '6b' tag to exit calibration
